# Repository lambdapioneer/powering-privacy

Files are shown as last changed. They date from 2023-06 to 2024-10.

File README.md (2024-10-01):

# Powering Privacy

This repository contains the artifacts from the paper: [Powering Privacy: On the Energy Demand and Feasibility of Anonymity Networks on Smartphones](https://www.usenix.org/conference/usenixsecurity23/).
It is has been submitted to the Artifact Evaluation process and has been awarded all badges we applied for.
You can find the [artifact appendix here](https://www.usenix.org/system/files/usenixsecurity23-appendix-hugenroth.pdf).

USENIX Artifact Evaluation Badge Available
USENIX Artifact Evaluation Badge Functional

## Overview

This repository contains:
- Documentation to build a hardware measurement kit
- Software and instructions to perform macro studies of long-running protocols
- Software and instructions to perform micro studies of individual operations
- Software and instructions to analyze results from these studies and generate plots
- Sample traces to allow evaluation without having to build the hardware kit

To verify these claims for the artifact evaluation process, please follow the [walkthrough.md](walkthrough.md) file.

## Requirements

You need access to a local computer running Ubuntu 20.04 with at least 16GiB of RAM and 200GiB of free disk space.
For the hardware setup, see the [bill of materials](hardware/bill-of-materials.md).

Further, we assume that you are comfortable doing the following tasks:
- Usage of standard developer tools (git, ssh, etc.)
- Basic familiarity with Python 3, Jupyter Notebooks, Android, and Rust
- Creating and running Docker images

We tested the setup with the following software:
- Ubuntu 20.04.6 LTS ([download here](https://releases.ubuntu.com/focal/))
- Python 3.8.10 (installed via apt-get)
- Docker 24.0.4 ([downloaded from here](https://docs.docker.com/engine/install/ubuntu/#install-using-the-convenience-script))
- Rust rustc 1.71.0-stable ([downloaded from here](https://rustup.rs/))
- Android Studio 2022.1.1 ([downloaded from here](https://developer.android.com/studio/archive))
- Gradle wrapper version 7.5 (installed with the tools within the `android` folder)

## Architecture overview

The following diagram shows the architecture of all components.
Note that for many of the steps, you do not need all of them.
The arrows indicate the direction of data flow, not necessarily the order of execution.

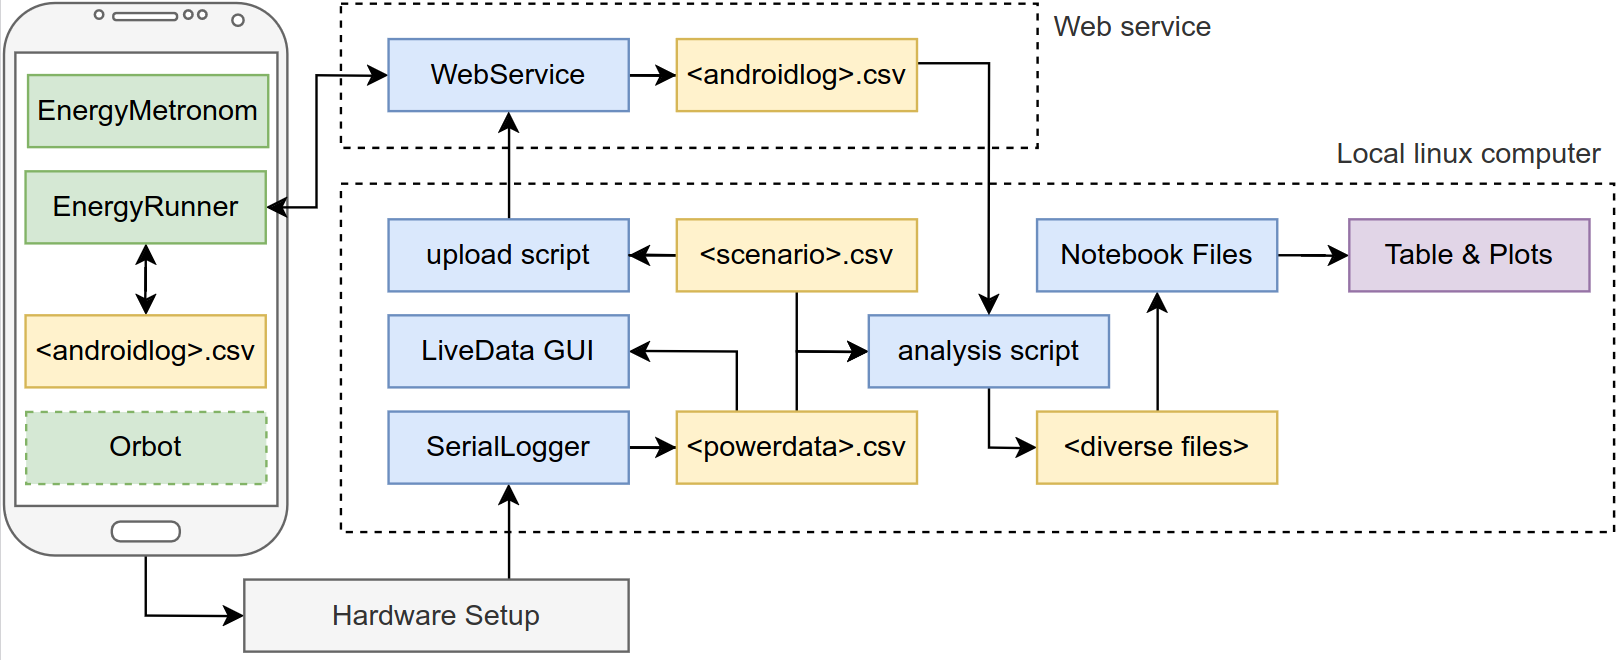
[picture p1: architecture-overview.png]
Architecture overview


The central component of the architecture is the hardware measurement kit.
This is described in [hardware/README.md](hardware/README.md) which contains both assembly and usage instructions.
The measurement kit is placed between the smartphone and the power supply and records the current and voltage over time.

The data is collected on the computer using the [rsoxy serial logger](rsoxy/README.md).
This Rust program reads the custom protocol via a serial connection of USB and stores it in a CSV file in the `/measurements` folder.

At any time the [LiveLogger](livelogger/README.md) can be used to view the so-far recorded power consumption.

## Macro studies

Macro studies measure the power consumption of a protocol over a long period of time.
For this the protocol is started manually on the smartphone, the display is turned off, and then `rsoxy` is started.
The recording is finished by terminating `rsoxy`.

Afterwards the `.csv` data can be analysed using any tool of your choice.
For example, using a Jupyter Notebook as shown in [notebooks/jupyter_tor.ipynb](notebooks/jupyter_tor.ipynb).

## Micro studies

Micro studies measure the power consumption of single operations.
For this, you first create a scenario file such as those in the [scenarios](scenarios) folder.

Then you upload the scenario to the [web service](webservice/README.md) using the [upload-scenarios.sh](scripts/README.md) script.
On the smartphone we use the [EnergyRunner](android/README.md) app to download the scenario.
A USB-to-go adapter and a USB-serial-adapter are used to connect the smartphone to the measurement kit to synchronize their clocks.
This process is described in the [walkthrough.md](walkthrough.md) document.

After the scenario has finished, the serial logger is terminated and on the Android phone the local logs (that contain the timings of individual operations) are uploaded to the web service.
The [analyze.py](scripts/README.md) script can then be used to download the logs, compare them to the local recordings, and break them into the individual sections for the operations.
The resulting `.csv` files can then be analysed using any tool of your choice.
For example, using a Jupyter Notebook as shown in [notebooks/jupyter_crypto_sections.ipynb](notebooks/jupyter_crypto_sections.ipynb).

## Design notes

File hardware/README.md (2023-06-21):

# Hardware

This directory contains all hardware-related files and documentation.

## Overview

The following schematic shows the overall setup. A power sensor (INA219) is placed between smartphone and battery to record the current power consumption. These results are read by an Arduino using the I2C protocol and the logged over USB to a computer. Optionally, a USB-to-go adapter and USB-to-serial component can be used to connect the smartphone to the Arduino to synchronize their clocks for the micro studies.

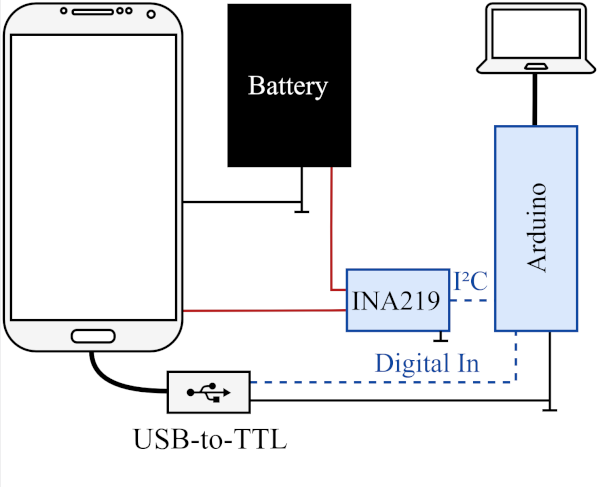
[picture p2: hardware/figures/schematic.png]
Schematic


The following pictures show the full setup in the real world.

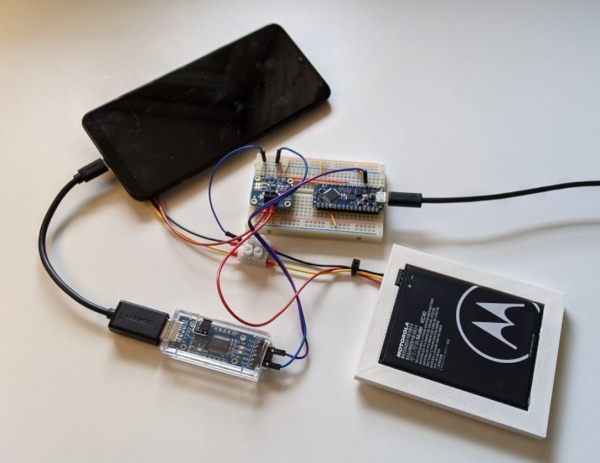
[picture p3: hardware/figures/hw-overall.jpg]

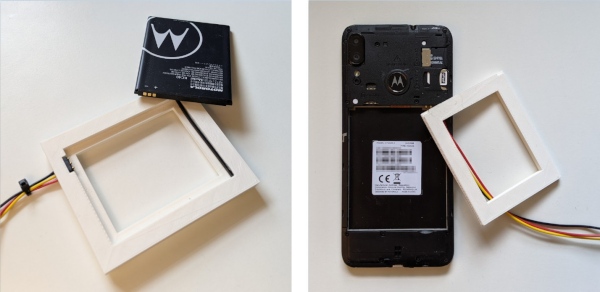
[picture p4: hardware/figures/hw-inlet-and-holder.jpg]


## Setup & Build

For building the hardware kit start by reading both the [Bill of Material](bill-of-materials.md) and the [Assembly Instructions](assembly-instructions.md) completely.

## Usage

Follow the instructions in the [walkthrough](../walkthrough.md) file to learn how to use this kit.

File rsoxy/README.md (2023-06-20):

# RSOXY

This is a fast Rust-based logger for the custom serial port protocol.
It reads from the connected Arduino and appends the data into the given file in a CSV format.
The data can be later read for analysis and during the recording one can `tail -f` that file or follow its updating content using the `livelogger`.

## Setup and build

Install Rust using [rustup](https://rustup.rs/).

For building the `serialport` dependency, the system must have the `libudev` installed.
On Ubuntu, you can do this as follows:

```
$ sudo apt install libudev-dev
```

Then build the project using Cargo:

```
$ cargo build --release
```

## Run

Once built, the binary can be run as follows:

```
$ ./target/release/rsoxy <FILE> [PORT]
```

where `<FILE>` is the path to the file to which the data will be written to and `[PORT]` is the optional path to the serial port device.

The (stderr) output should start with debug information similar to the following:

```
>> # Compiled on 'Apr 13 2021' at '16:13:53'
>> # mps:2897 (limit:2500)
>> # input pin: 14
>> start
```

## Docker

Alternatively, you can build and run the project using Docker. However, this tends to be a bit more quirky than building and running it directly on the host machine.

The following commands build the Docker image and run the container with the serial port device mounted and the measurements volume mounted as well.

```
$ docker build -t rsoxy .
$ docker run -it --volume=$(pwd)/../measurements:/measurements --device=/dev/ttyACM0 --rm rsoxy rsoxy /measurements/myexperiment.csv
```

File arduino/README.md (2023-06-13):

# Arduino

This folder contains the software and instruction to flash the Arduino for the hardware setup.

## Setup and build

Install the Arduino IDE. Then install the Adafruit INA219 library by going to `Tools > Manage Libraries` and searching for `Adafruit INA219`:

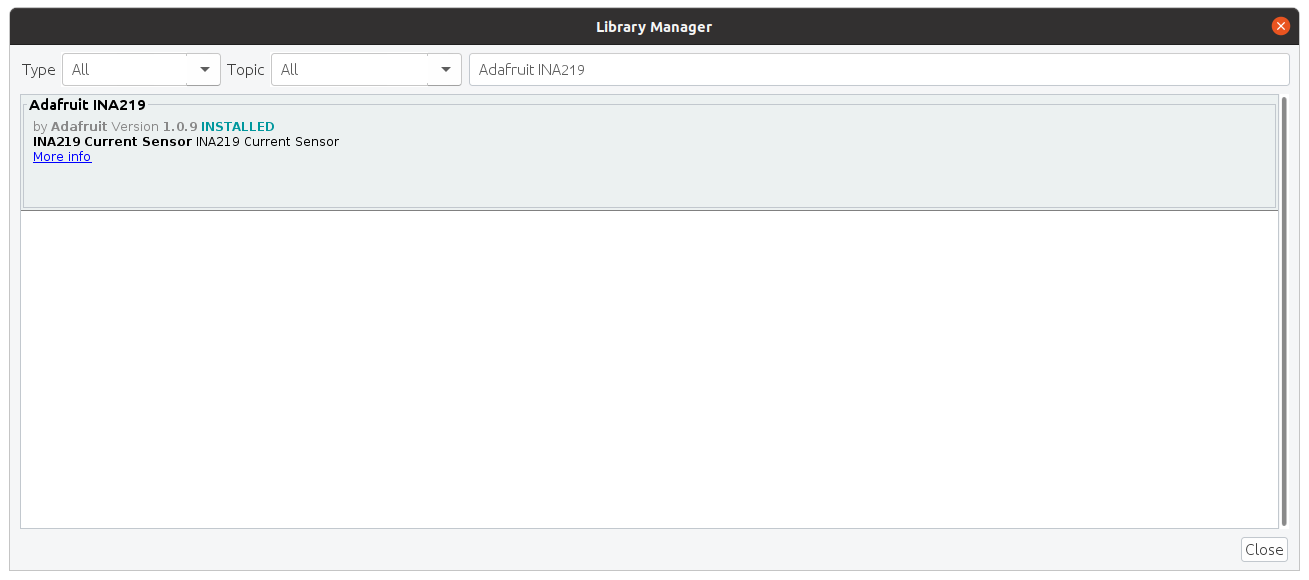
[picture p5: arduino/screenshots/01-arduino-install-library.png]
Installing library


Then open the `logger.ino` file in the Arduino IDE and flash it to the Arduino. Follow the instructions for the other hardware setup in [hardware/README.md](../hardware/README.md).

Alternatively, you can use the `arduino-cli` to build and flash the Arduino:

```bash
$ export FQDN="arduino:megaavr:nona4809"
$ arduino-cli board list
$ arduino-cli compile --fqbn $FQDN logger
$ arduino-cli upload -p /dev/ttyACM0 --fqbn $FQDN logger
```

## Run

When all components have been connected, you can start the Arduino by connecting it to a free USB port on your computer.
Use the [rsoxy](../rsoxy/README.md) serial logger to verify that everything is working correctly.
In particular, watch out for messages that indicate that the INA219 was not found.
The Arduino should reset every time the serial connection is re-started which allows to just restart the serial logger without having to re-connect the Arduino.

## Optional: custom INA219 calibration

By default the `logger.ino` uses a 16V/400mA calibration for the INA219.
However, 400mA might be limiting, and we can increase the range to 800mA as well as increasing the sampling frequency by modifying the library.

To do so, find the libraries folder of the Arduino IDE, open the file `libraries/Adafruit_INA219/Adafruit_INA219.cpp`, and add the following lines below the other `setCalibration_` functions:

```cpp
void Adafruit_INA219::setCalibration_CUSTOM() {
  // 16V & 800mA
  ina219_currentDivider_mA = 20;
  ina219_powerMultiplier_mW = 1.0f;

  ina219_calValue = 8192;
  Adafruit_BusIO_Register calibration_reg =
      Adafruit_BusIO_Register(i2c_dev, INA219_REG_CALIBRATION, 2, MSBFIRST);
  calibration_reg.write(ina219_calValue, 2);

  uint16_t config = INA219_CONFIG_BVOLTAGERANGE_16V |
                    INA219_CONFIG_GAIN_2_80MV |
                    INA219_CONFIG_BADCRES_11BIT |
                    INA219_CONFIG_SADCRES_11BIT_1S_276US |
                    INA219_CONFIG_MODE_SANDBVOLT_CONTINUOUS;

  Adafruit_BusIO_Register config_reg =
      Adafruit_BusIO_Register(i2c_dev, INA219_REG_CONFIG, 2, MSBFIRST);
  config_reg.write(config, 2);
}
```

Also add `void setCalibration_CUSTOM();` to `libraries/Adafruit_INA219/Adafruit_INA219.h`.
Then uncomment the relevant line (l. 53) in `logger.ino`, comment the other old calibration, and flash the Arduino again.

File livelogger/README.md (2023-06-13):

# LiveLogger

The LiveLogger is a GUI interface using Java2D which displays energy measurements.

## Setup and build

Install a JDK 8 or newer. On Ubuntu you do this by running:

```
$ sudo apt-get install openjdk-8-jdk
```

The LiveLogger builds and runs using the Gradle build tooling.
On the first execution, it will first download a recent Gradle version and all dependencies.

Execute the following command to build the live logger:

```
$ ./gradlew build
```

## Run

Execute the following command to run the live logger:

```
$ ./gradlew run
```

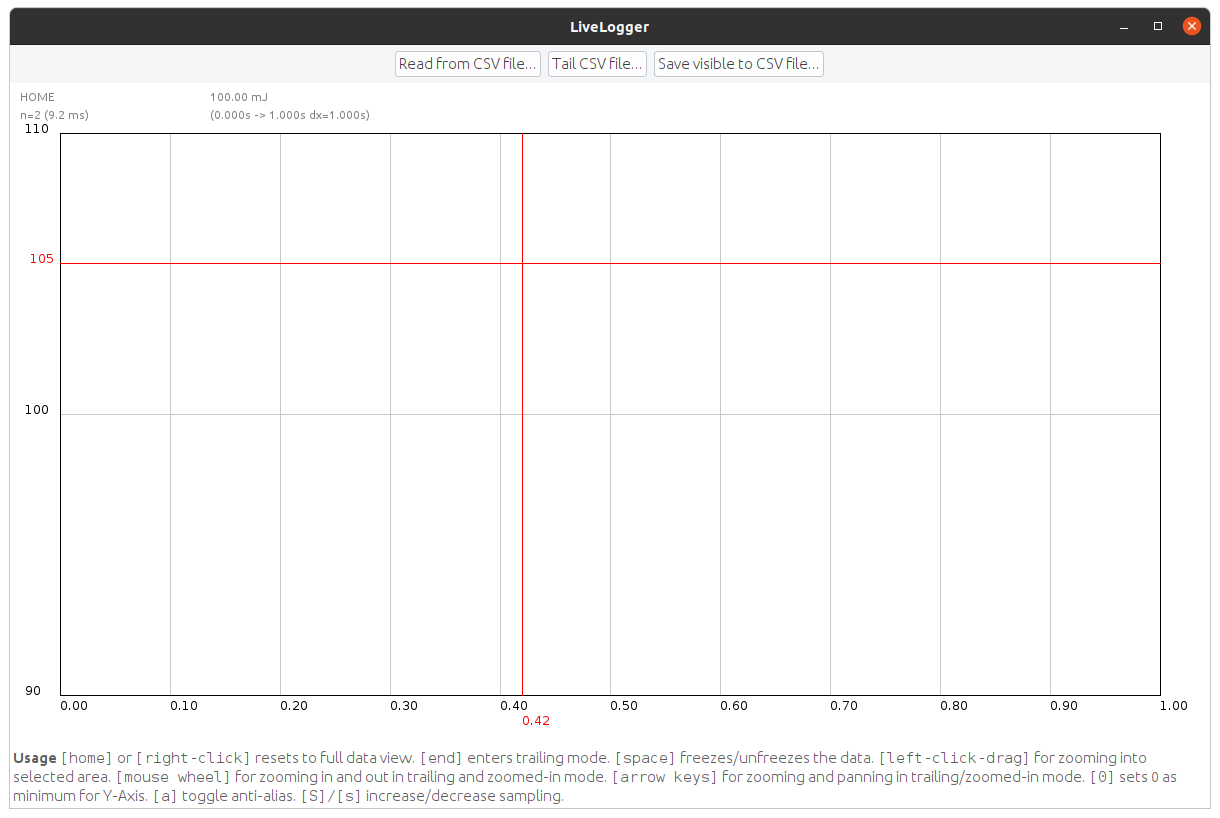
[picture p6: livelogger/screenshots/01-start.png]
Screenshot of the app after start


Once started use the you can use the top buttons to _open_ a recorded file or _tail_ a file that is currently being recorded.
The latter will follow the file like `tail -f`, i.e., continuously read data as it is being appended.

With the data you can use the mouse to select a region of interest.
The plot will then zoom into the selected region.

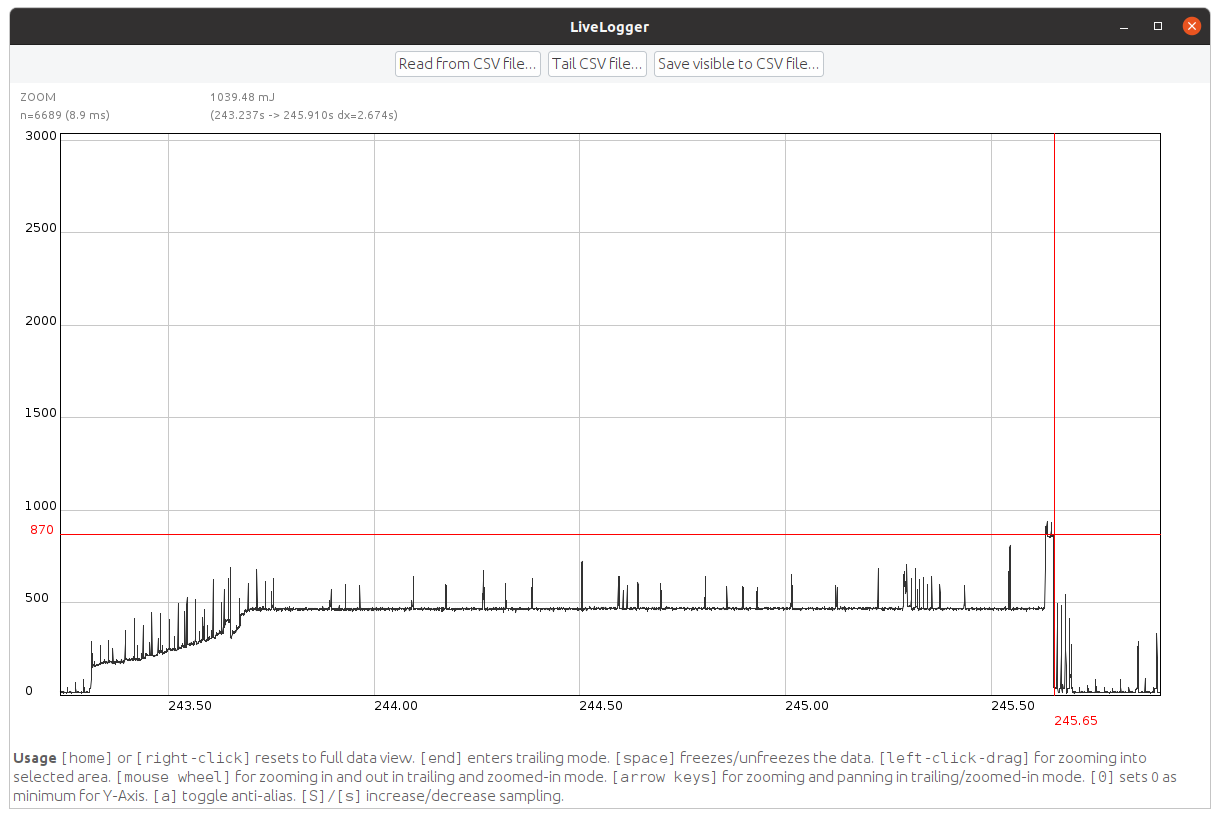
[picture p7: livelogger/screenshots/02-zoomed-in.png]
Screenshot of the app showing a zoomed-in region


Pressing the `HOME` key or a right-click will reset the zoom.
You can also use the left and right arrow keys to move the zoom window.
You can zoom in and out using the mouse wheel and the up and down arrow keys.

When tailing a file you can set the zoom to automatically follow the end of the file by pressing the `END` key.
The current mode is shown in the top-left corner: `HOME`/`ZOOM`/`TAILING`.

The top also shows some basic statistics about the selected region.
Below the mode indicator you can see the number of samples of the current region and how long the draw routine takes.
To the right details about the currently displayed region are shown which include the total energy consumption and the time span.

When displaying many samples, the draw routine can take a long time.
You can improve the performance by turning-off anti-aliasing (key `a`) or increasing the sampling (`shift`+`s`).
However, when saving the currently visible region, the sampling is taken into account, i.e. the saved data will have less resolution.

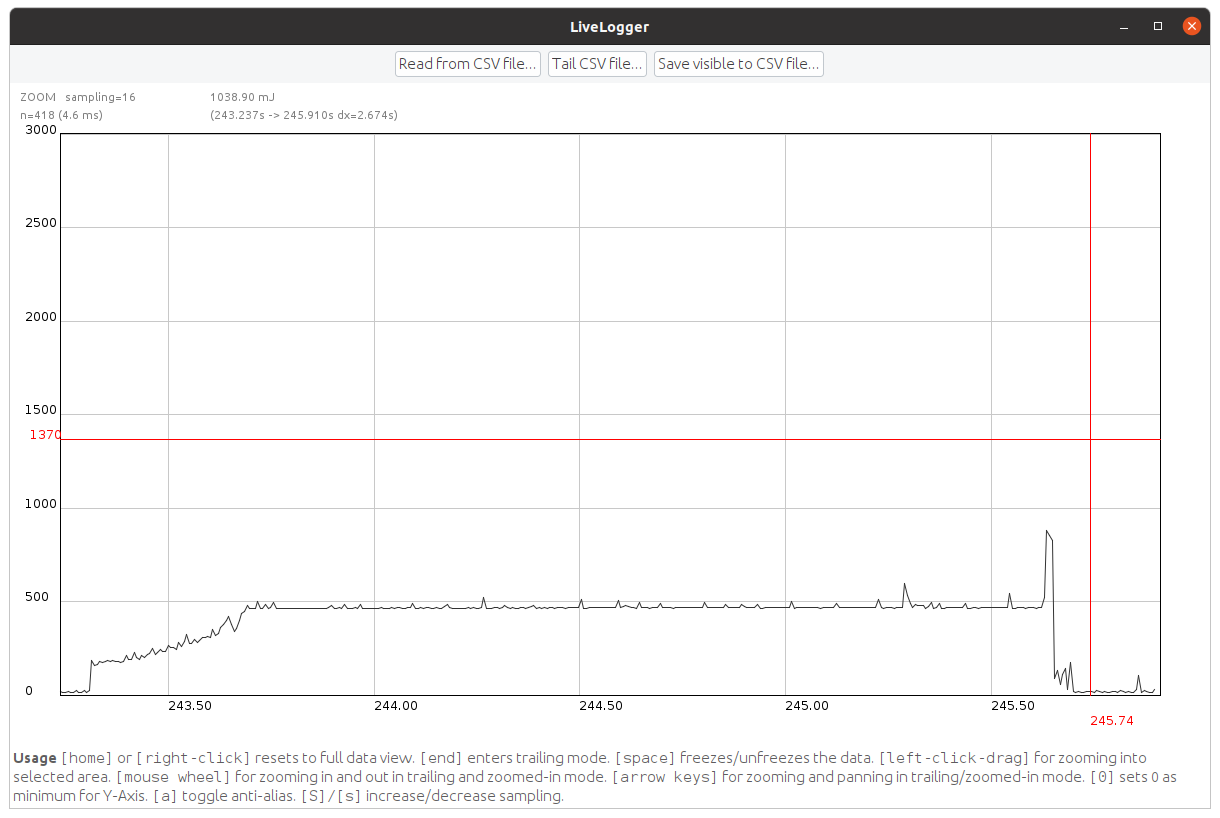
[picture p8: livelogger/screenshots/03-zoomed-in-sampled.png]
Screenshot of the app showing a zoomed-in region while sampled


## Docker

There is no Dockerfile for this component, as the GUI is not really useful in a container.

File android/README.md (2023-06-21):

# Android

This folder contains all Android related project code including libraries and apps.

It consists of two library modules and two app modules.
The `lib_sphinxkt` is a wrapper around the Rust [Sphinx library](https://github.com/nymtech/sphinx).
The `lib_common` library implements many operations used by both apps and depends on the `lib_sphinxkt` library.
The `app_metronom` app allows to execute operations at regular intervals (e.g. opening a web page every 60 seconds).
This is used e.g. for the Tor and VPN macro studies.
The `app_energy_runner` allows to run scenarios files.
These are downloaded from the [web service](../web_service/README.md) and then executed.
This app also synchronizes with the data logger using USB serial and can later upload the timing information for the individual operations.

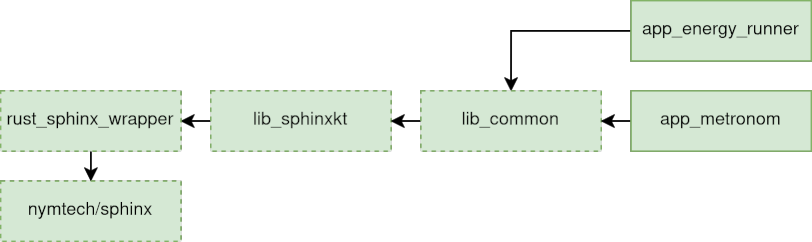
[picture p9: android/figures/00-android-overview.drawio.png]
Overview of components


This folder also contains a `orbot.*.patch` file that can applied to the Orbot source code to add an option for disabling connection padding. See Step E2.2 in the [walkthrough](../walkthrough.md) for details.

## Setup and build

Install Android Studio 2022.2.1 (or newer) and open the project.

The `lib_sphinxkt` uses the Mozilla "Rust Android Gradle Plugin" to build and link the Rust code.
Follow their [setup instruction](https://github.com/mozilla/rust-android-gradle#usage) to setup all dependencies.
You might find that it helpful to first try your local Rust setup with the simpler [rsoxy serial logger project](../rsoxy/README.md).

Before building, update the `configuration.properties` file with the IP address for the web service.

Once you opened the project and installed the Rust Android plugin dependencies, you can build the project (Build > Make Project).

Alternatively, you can build the project from the command line:

```
$ ./gradlew assembleDebug
```

## Run

You can install the `app_metronom` using the following command:

```
./gradlew app_metronom:installDebug
```

After install find the app in the launcher drawer and drag it to the start screen.
Go to the Android app info (usually long press on the icon), navigate to "Advanced" and enable "Display over other apps".
This is required to show the overlay window for the web browsing task.
One starting the app you should see a screen like the following below.
Select a short pause, click `Start`, and observe after 60 seconds that an overlay window appears that loads a website and closes on finish.

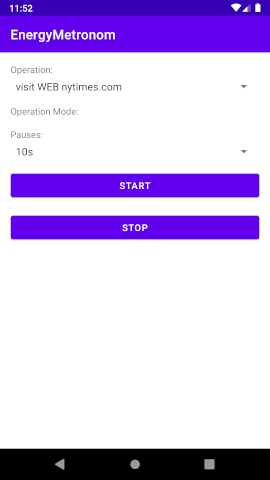
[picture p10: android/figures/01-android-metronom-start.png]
app_metronom after start
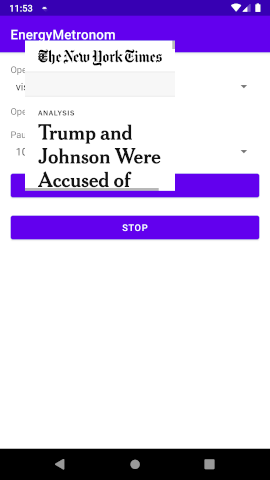
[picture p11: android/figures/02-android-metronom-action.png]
app_metronom during_web_page_load
 

You can install the `app_energy_runner` using the following command:

```
./gradlew app_energy_runner:installDebug
```

After install find the app in the launcher drawer and drag it to the start screen.
Go to the Android app info (usually long press on the icon) and deactivate any battery optimization that might interfere with running the app in the background for long periods of time.
One starting the app you should see a screen like the following below.
The details on how to use the app are given in the complete AE run-through instructions.

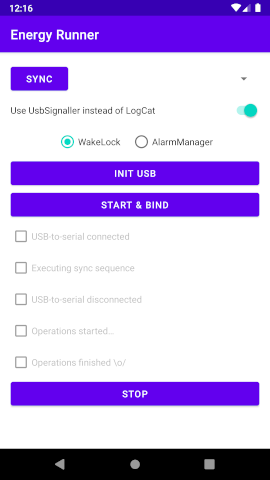
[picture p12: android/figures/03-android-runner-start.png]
app_runner after start


## Docker

There is no Dockerfile for this component, as there is no reliable image for Android development that includes Rust components.

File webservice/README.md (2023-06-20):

# Webservice

The webservice can be run locally or remotely and provides a REST API to sync scenarios to the Android device and to sync the results back.

> **Warning**
> Note that this is a very simple implementation and does not provide any security or authentication.
Hence, if the service is run from a publicly accessible server, it should be protected by a reverse-proxy with authentication or similar.
See the sample .htpasswd file for the sample user/password configuration (user:uyaeNiyaighiu4HaingohShee2ie9ahs).

## Setup and build

Ensure that a version of Python 3 is installed.

First setup the virtual environment and install all required dependencies:

```
$ python3 -m venv venv
$ source venv/bin/activate
(env)$ pip install -r requirements.txt
```

## Run

Start the webservice with the virtual environment activated as follows:

```
(env)$ FLASK_APP=app.py flask run
```

You can verify that the service is running correctly by opening http://127.0.0.1:5000/energy/android_logs.zip which should download an empty .zip archive.

Update the scripts and the Android apps with the correct IP address of the webservice and authentication details (if applicable).

## Docker

Alternatively, you can build and run the project using Docker:

```
$ docker build --network=host -t webservice .
$ docker run -it --rm --volume=storage:/usr/src/webservice/measurements --publish=5000:5000 webservice
```

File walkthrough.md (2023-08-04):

# Artifact Evaluation Walkthrough

This document walks you step-by-step through all three artifact evaluation experiments:

- **E0:** Building and testing all critical components including the hardware kit, rsoxy, and the live logger.
- **E1:** Performing a micro study to measure individual cryptographic operations
- **E2:** Performing a macro study to measure the performance of Tor vs direct website access over WiFi

The experiments provide time estimates in _human-hours_ which are the total work time, which can be interrupted, and _experiment-hours_ which are the durations of the experiments which cannot be interrupted.

## Requirements & preparations

You will need a local computer with:
- A recent Ubuntu version (we tested 20.04)
- At least 16 GiB RAM
- At least 200 GiB free disk space
- A free USB port to connect to the Arduino
- A WiFi where you can connect the smartphone and the computer to the same network

In preparation for building the individual components, you should install the following dependencies before beginning:  

- Docker; see the [Docker documentation](https://docs.docker.com/engine/install/ubuntu/)
- Rust; see the [rustup website](https://rustup.rs/)
- Python 3; it is usually preinstalled; otherwise see the Ubuntu documentation
- Android Studio; see the [Android Studio website](https://developer.android.com/studio/install)

If you use the sample traces, see [measurements/sample-traces/README.md](measurements/sample-traces/README.md) for instructions on how to extract and import them.

## E0: Building and testing all critical components (2-20 human-hours + 1×1 experiment-hour)

In this experiment you will first (optionally) build the hardware kit and then use it with the `rsoxy` and `livelogger` programs to record a test trace. This will ensure that all components are working correctly and that you are familiar with the process of recording a trace.

### E0.1: Building the hardware kit (optional: 9 human-hours, 12 hours wait time)

> **Note**
> You can skip this step if you have been provided the hardware kit or are using the sample traces.

First read the [bill of materials](hardware/bill-of-materials.md) to see what you need to build the hardware kit. Then follow the [assembly instructions](hardware/assembly-instructions.md) to build the hardware kit.

Then follow the [Arduino setup instructions](arduino/README.md) to program the Arduino.

### E0.2: Test rsoxy and live logger (1 experiment-hour)

Follow the instructions in the [rsoxy/README.md](rsoxy/README.md) to build rsoxy. 
Follow the instructions in the [livelogger/README.md](livelogger/README.md) to build livelogger. 

Connect the Arduino still to the computer, ensure that the final assembly of the hardware kit with the battery in the battery holder and the inlet inside the smartphone, and turn on the smartphone.
Start recording a test trace with `rsoxy` in `measurements/e0-test-trace.csv`.

> **Note**
> If you use the sample traces, copy the `e0/demo_trace_wifi_display_onoff_20230620_1600.csv` file to your `/measurements` directory.

The first lines of (stderr) output from `rsoxy` should look like this:

```
>> # Compiled on 'June 1 2023' at '13:37:42'
>> # mps:2897 (limit:2500)
>> # input pin: 14
>> start
```

Open the `livelogger` and tail the current measurement file. You should see the data being logged in real-time and change as you use the device. For instance, try changing the display brightness or turn the display off and observe how it enters low-power mode after a few seconds. If you are using the sample file, you should see high power consumption at the beginning (with a small dip where the brightness of the display is changed), and then lower power after the display is turned off.

The GUI should look similar to this:

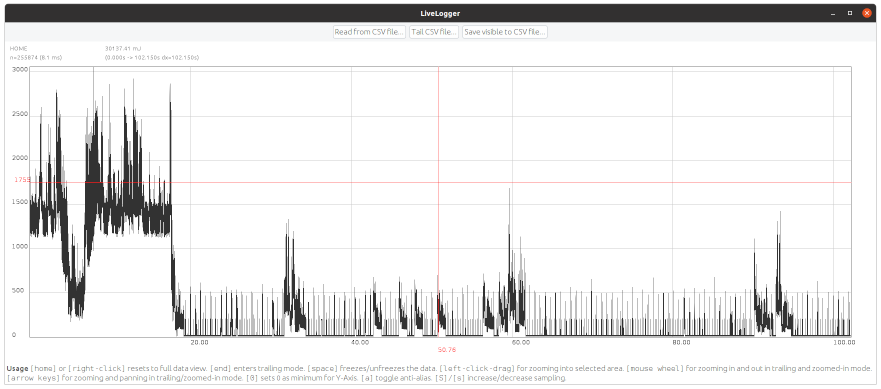
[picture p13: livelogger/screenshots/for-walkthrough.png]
livelogger GUI


If you got to here, well done! Most of the dependencies and configurations are now set up and you can proceed to the next steps. If built your own hardware kit, you can be quite confident that it is working correctly.

## E1: Micro study of cryptographic operations

In this experiment you use the most complex experiment setup to first load a scenario to the Android phone, then record it with synchronized clocks, download and combine all logs, and then re-create Table 2 from the paper.

> **Note**
> If you use the sample traces, copy the files from `e1/` file to your `/measurements` directory and skip to step E1.6.

### E1.1: Create the scenarios

The scenarios have been created for you, and you can inspect the files [scenarios/crypto_asymmetric.scenario](scenarios/crypto_asymmetric.scenario) and [scenarios/crypto_hashing.scenario](scenarios/crypto_hashing.scenario).

### E1.2: Start the webservice and upload the scenarios (1 human-hours)

Next we will build and run the webservice on the local computer. Alternatively, if could be run on a remote server, but this is more complicated and not necessary for the artifact evaluation. Follow the instructions in [webservice/README.md](webservice/README.md) to build and run the webservice. Either the local Python 3 approach or using Docker is fine.

However, verify that it is reachable from the Android phone when connected to the same WiFi. Try opening `http://<computer-wifi-ip-here>:5000/energy/android_logs.zip` in the browser on the Android phone and verify that it downloads an empty zip file.

Keep the webservice running for the rest of the experiment.

Follow the instructions in [scripts/README.md](scripts/README.md) to run the `upload_scenarios.sh` script.

### E1.3: Build and install the Android app (2 human-hour)

Follow the instructions in [android/README.md](android/README.md) to build and install the `energy_runner` Android app. For this you might need to [enable the developer mode](https://developer.android.com/studio/debug/dev-options) on the smartphone.

This is also a good time to remove or disable all unwanted apps so that they do not interfere with the experiment. Also, long press on the app, go to the app info, and disable _all_ battery optimizations. This is important to ensure that the app is not killed in the background.

Once the app is started, press the `SYNC` button to download the scenarios. They should appear in the top list. If you see an error, check the logs in the Android Studio logcat console.

Connect the USB-to-serial adapter to the USB-OTG cable and plug it into the smartphone. You should see a popup that asks you to start EnergyRunner. Confirm and select the box to always use it. Remove the adapter and force-stop the app.

### E1.4: Run the experiments (2×1 experiment-hour)

Connect the USB-to-serial adapter to the breadboard as per Step 6 in the [assembly instructions](hardware/assembly-instructions.md). Connect the USB-OTG with the adapter and the smartphone. This should now start the EnergyRunner app automatically.

Once inside the app press `SYNC` and then enter flight mode to to avoid any background network traffic. Select the scenario that you want to run first. Press `INIT USB` after which the one indicator LED on the Arduino should turn off.

On your local computer start `rsoxy` to record a file into `measurements/<scenario-name>_<yyyymmdd>_<hhmm>_raw.csv` (e.g. `measurements/crypto_asymmetric_20230620_1600_raw.csv`). The exact naming and semi-accurate datetime is important as the analysis script will use the filenames to determine which recordings belong together.

Optionally, start `livelogger` to tail the file and observe the recording as it progresses.

On the smartphone press `START` and turn off the display.

The smartphone should say "USB is connected" once it starts using the serial adapter. On the computer you should be able to observe the synchronization pattern as 1s and 0s in the stderr output of `rsoxy`.

Once the smartphone says "Sync is done", disconnect the USB-OTG cable. The smartphone should soon after confirm this by saying "USB is disconnected". The text-to-speech output is used to avoid having to turn on the screen.

Now wait patiently while the experiment is under way. Both experiments should take around 30 minutes to complete. Once the scenario is completed, the smartphone will repeatedly say "Operations finished".

Once finished, stop `rsoxy` (CTRL+C) and on the Android phone press `STOP`. Turn on WiFi and press `SYNC` to upload the Android logs to the webservice. If the upload fails, it is possible to retry multiple times as the log files are stored locally as well.

Repeat the experiment for the other scenario.

### E1.5: Download and analyze the logs (1 human-hour)

On the computer run the `analyze.py` script (see [scripts/README.md](scripts/README.md)) to download and analyze the logs. It takes the scenario filename as its mandatory command line argument.

Once finished, for every scenario name, there should be the following files in the `measurements` directory:

- `_raw.csv`: the power measurements created with `rsoxy`
- `_android.csv`: the Android logs created by the EnergyRunner app
- `_trace.csv`: additional Android logs created by the EnergyRunner app
- `_info.json`: JSON file with the clock difference information
- `_sections.csv`: the timing information and calculated energy consumption for each operations.

For the final step, the Jupyter Notebooks will only use the `_sections.csv` file, but the other files are useful for debugging and verification.

### E1.6: Run Jupyter Notebooks (1 human-hour)

Follow the instructions in [notebooks/README.md](notebooks/README.md) to run the `notebooks/jupyter_crypto_sections.ipynb` notebook. If you use your own measurements, update the filenames in the second cell.

The output of the table should look like this:

```latex
\midrule
Gen RSA-1024 & 116.47 & 76.36 \\ 
Gen RSA-2048 & 796.05 & 597.84 \\ 
Gen RSA-4096 & 2898.43 & 2042.77 \\ 
Sign RSA-1024 & 1.88 & 0.35 \\ 
Sign RSA-2048 & 6.22 & 1.22 \\ 
Sign RSA-4096 & 26.73 & 4.68 \\ 
Verify RSA-1024 & 0.34 & 0.10 \\ 
Verify RSA-2048 & 0.50 & 0.08 \\ 
Verify RSA-4096 & 0.75 & 0.10 \\ 
\midrule
Gen EC-224 & 1.11 & 0.06 \\ 
Gen EC-256 & 0.51 & 0.05 \\ 
Gen EC-384 & 2.65 & 0.07 \\ 
Gen EC-521 & 5.25 & 0.27 \\ 
Sign EC-224 & 1.43 & 0.15 \\ 
Sign EC-256 & 0.83 & 0.18 \\ 
Sign EC-384 & 3.24 & 0.16 \\ 
Sign EC-521 & 6.27 & 0.10 \\ 
Verify EC-224 & 1.52 & 0.05 \\ 
Verify EC-256 & 1.54 & 0.08 \\ 
Verify EC-384 & 3.43 & 0.07 \\ 
Verify EC-521 & 6.74 & 0.15 \\ 
\midrule
Sphinx (1x) & 9.66 & 0.31 \\ 
Sphinx (10x) & 86.34 & 8.07 \\ 
Sphinx (100x) & 842.44 & 11.40 \\ 
```

## E2: Macro study of Tor

In this experiment you measure long protocol runs and save them in individual files. In particular, you will measure the energy consumption of Orbot over WiFi for both the idle and web browsing scenarios and then compare it with not using Tor.

> **Note**
> If you use the sample traces, copy the files from `e2/` file to your `/measurements` directory and skip to step E2.4.

### E2.1: Install EnergyMetronom (1 human-hour)

Follow the instructions in [android/README.md](android/README.md) to build and install the `metronom` Android app. Afterwards, long press on the app and go to the app info. There, enable "Display over other apps" which is required to show the overlay window for the web browsing task. Also, and disable _all_ battery optimizations. This is important to ensure that the app is not killed in the background.

Test the app by selecting the settings to open the news website every 10 seconds and observe that an overlay window appears and disappears.

### E2.2: Install Orbot (1 human-hour)

Clone the [Orbot repository](https://github.com/guardianproject/orbot/) and checkout commit `b06e05c4` (version 16.6.0-RC4). Install the app following their instructions and using `./gradlew installFullpermRelease`. As this is a release build, you might need to create a signing key first (see https://developer.android.com/studio/publish/app-signing#generate-key).

Test the app on the device. In particular, enable VPN mode and verify that you can access regular websites through Tor. This can be done by opening https://check.torproject.org/ in the phone browser.

In the setting make sure to _enable_ "Connection padding" and _disable_ "Reduced connection padding". This ensures that regular connection padding is forced on. 

> **Note**
> For our experiments we have written a [patch file](android/orbot-add-setting-to-disable-connection-padding.patch) that adds a new setting to disable connection padding. This is not needed for the walkthrough, but you might want to apply it if you run your own experiments.

### E2.3: Run the experiments (4×1 experiment-hour)

Now you will run four experiments to measure the power consumption of all combinations. In the terminology of the later Jupyter notebook scripts we will have:

- `radio`:
  - `wifi`
- `activity`:
  - `idle`
  - `web`
- `networks`
  - `direct` (i.e. no Tor)
  - `fullpad` (i.e. Tor with full padding)

As you record the power consumption with `rsoxy`, make sure to name them according to this scheme: `measurements/tor_<radio>_<activity>_<network>.csv` (e.g. `measurements/tor_wifi_idle_direct.csv`). This is important as the analysis script will use the filenames to find the recordings.

As you record you can use the livelogger tool to observe the current measurements to quickly identify andy issues.

Now run the following experiments:

- `activity=idle`
  - `network=direct`
    - Turn off the display, wait 30 seconds and then record the energy measurements for at least 10 minutes.
  - `network=fullpad`
    - Enable Tor in VPN mode with the settings from above. Turn off the display, wait 30 seconds and then record the energy measurements for at least 10 minutes.
- `activity=web`
  - `network=direct`
    - Start the metronom with visiting the website every 60 seconds. Wait until it was displayed successfully one time. Then turn off the display, wait 30 seconds and then record the energy measurements for at least 10 minutes.
  - `network=fullpad`
    - Enable Tor in VPN mode with the settings from above. Start the metronom with visiting the website every 60 seconds. Wait until it was displayed successfully one time. Then turn off the display, wait 30 seconds and then record the energy measurements for at least 10 minutes.

Afterwards, you should have the following files (each around 20-25 MiB in size) in your measurements directory:

```
tor_wifi_idle_direct.csv
tor_wifi_idle_fullpad.csv
tor_wifi_web_direct.csv
tor_wifi_web_fullpad.csv
```
  
### E2.4: Analyse the measurements (1 human-hour)

Follow the instructions in [notebooks/README.md](notebooks/README.md) to run the `notebooks/jupyter_tor.ipynb` notebook.

The graph output should look like this:

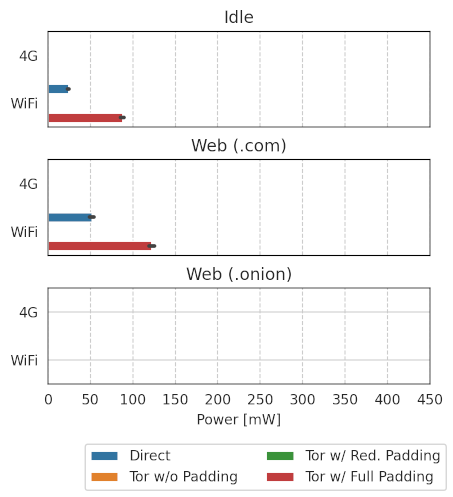
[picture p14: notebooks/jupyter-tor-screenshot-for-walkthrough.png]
Plot output


And the table output should look like this:

```latex
\multicolumn{4}{c}{\textit{Idle}}\\
\midrule
4G & Direct & nan & nan\% \\ 
4G & Tor w/o Padding & nan & nan\% \\ 
4G & Tor w/ Red. Padding & nan & nan\% \\ 
4G & Tor w/ Full Padding & nan & nan\% \\ 
\midrule
WiFi & Direct & 23.4 & 0.3\% \\ 
WiFi & Tor w/o Padding & nan & nan\% \\ 
WiFi & Tor w/ Red. Padding & nan & nan\% \\ 
WiFi & Tor w/ Full Padding & 87.3 & 1.1\% \\ 
\midrule
\multicolumn{4}{c}{\textit{Web (.com)}}\\
\midrule
4G & Direct & nan & nan\% \\ 
4G & Tor w/o Padding & nan & nan\% \\ 
4G & Tor w/ Red. Padding & nan & nan\% \\ 
4G & Tor w/ Full Padding & nan & nan\% \\ 
\midrule
WiFi & Direct & 52.0 & 0.6\% \\ 
WiFi & Tor w/o Padding & nan & nan\% \\ 
WiFi & Tor w/ Red. Padding & nan & nan\% \\ 
WiFi & Tor w/ Full Padding & 122.9 & 1.5\% \\ 
\midrule
\multicolumn{4}{c}{\textit{Web (.onion)}}\\
\midrule
4G & Direct & nan & nan\% \\ 
4G & Tor w/o Padding & nan & nan\% \\ 
4G & Tor w/ Red. Padding & nan & nan\% \\ 
4G & Tor w/ Full Padding & nan & nan\% \\ 
\midrule
WiFi & Direct & nan & nan\% \\ 
WiFi & Tor w/o Padding & nan & nan\% \\ 
WiFi & Tor w/ Red. Padding & nan & nan\% \\ 
WiFi & Tor w/ Full Padding & nan & nan\% \\ 
\midrule
```

Note that some bars and entries are missing when comparing to the table. These are because we only recorded a subset of the parameter space.

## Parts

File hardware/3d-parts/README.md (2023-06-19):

# 3D Printed Parts

Both hardware parts are designed using [OpenSCAD](https://openscad.org/) and maintained within the respective `.scad` files.
From these the STL files are rendered.
You should use the slicing tool that is recommended for your 3D printer to generate the respective `.gcode` files.
For reference, the folder contains some for the Pruse i3 MK3S.

## Renderings

This is the **battery replacement** which goes into the phone. Note the corners that allow it to snap into place. Also, there are three cut-outs for the contacts.

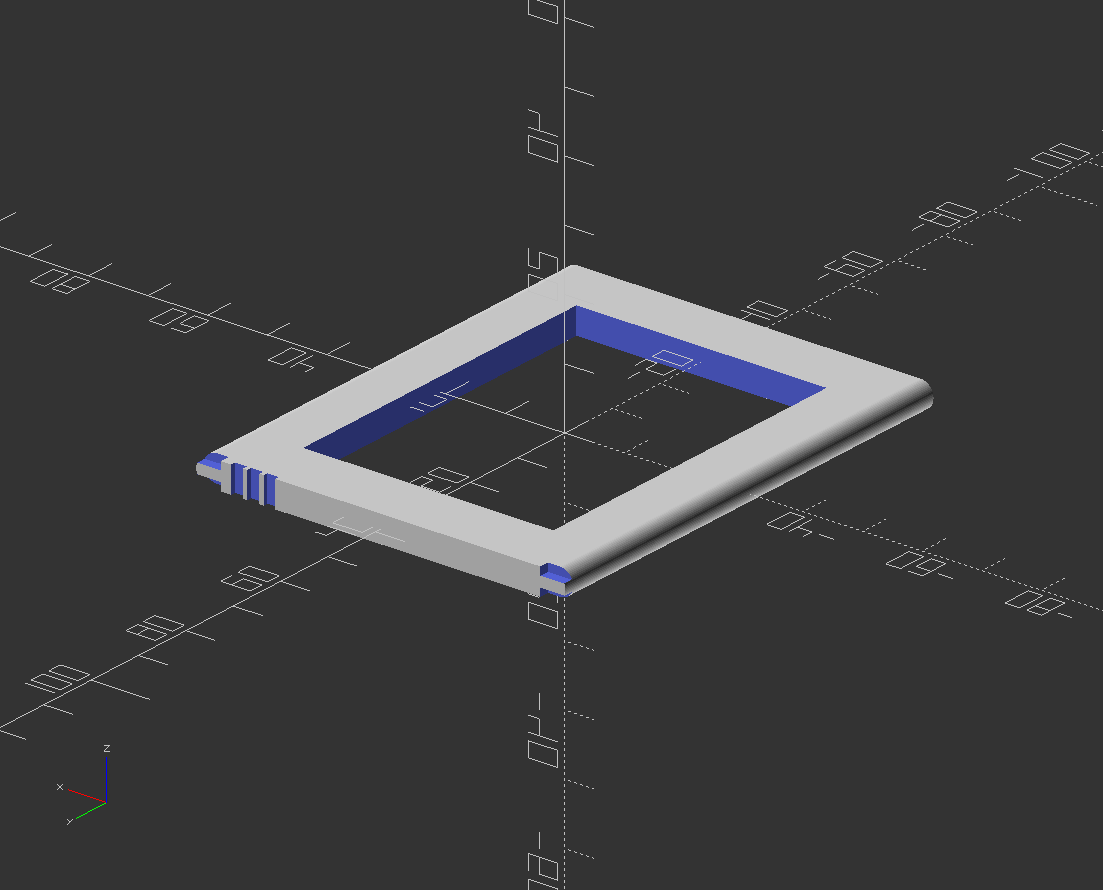
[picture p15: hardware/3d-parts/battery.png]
The battery replacement


This is the **battery holder** which holds and connects the actual battery. Note the hole (front left) where the battery connector slides in.

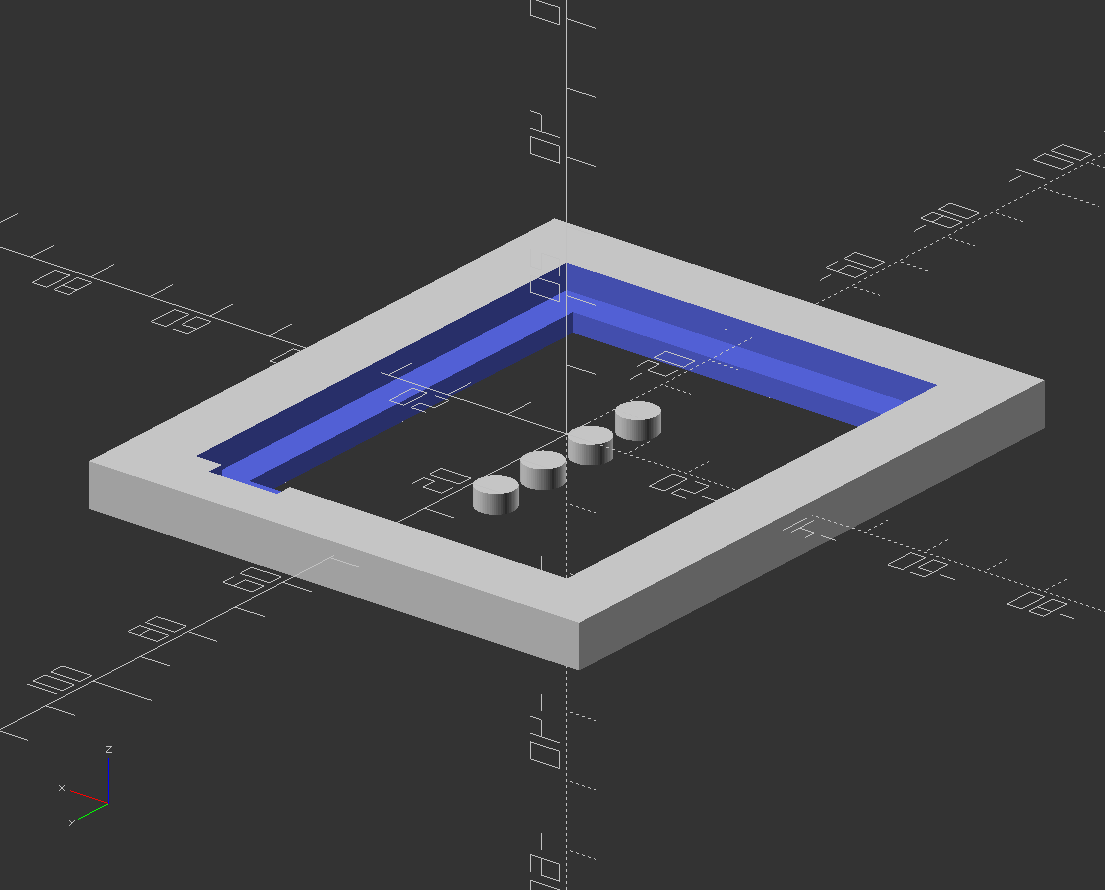
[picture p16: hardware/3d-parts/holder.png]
The battery holder


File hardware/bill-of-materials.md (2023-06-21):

# Bill of materials

This document lists all parts that are required for the project. It is split into three sections: parts, tools and consumables.
We believe that the required tools and consumables are commonly available in most makerspaces.

## Parts

The links are just to help disambiguate the parts. They are available from various sources.

| Part | Quantity | Comment & Link |
| ---- | -------- | -------------- |
| Arduino Nano Every | 1 | [Link to arduino.cc](https://docs.arduino.cc/hardware/nano-every) |
| INA219 | 1 | On a breakout board; [link to adafruit.com](https://www.adafruit.com/product/904) |
| Breadboard | 1 | Half-size; [link to adafruit.com](https://www.adafruit.com/product/4539) |
| Leaf battery connector | 1 | TE 1981061-1; [link to te.com](https://www.te.com/usa-en/product-1981061-1.html) |
| USB-to-serial adapter | 1 | With FTDI FT232RL chip; [link to amazon.com](https://www.amazon.com/gp/product/B07BBPX8B8/)
| USB OTG cable | 1 | For example: [link to amazon.com](https://www.amazon.com/UGREEN-Adapter-Samsung-Controller-Smartphone/dp/B00LN3LQKQ/) |
| Motorola Moto E6 Plus | 1 | Available from third-party vendors; [link to gsmarena.com](https://www.gsmarena.com/motorola_moto_e6_plus-9831.php) |

## Tools

| Tool | Comment |
| ---- | -------------- |
| Soldering station |  |
| 3D printer | We use a Prusa i3 |
| Wire cutter | |
| Crimping tool | (for Ferrules) |
| Wire stripper | (optional) |
| Tweezers ||
| Screwdrivers | Various small ones|

## Consumables

| Part | Quantity | Comment & Link |
| ---- | -------- | -------------- |
| Breadboard wires | various ||
| Wires | 2m | For connecting battery and smartphone, at least 16 AWG |
| Ferrules | 10 | For the above mentioned wires |
| 6.8kΩ resistor | 1 | |
| Male to female jumper wires | 2 | |
| Terminal connector blocks | 3 | Small ones (~5A) |
| SD card (adapter) | 1 | We use the connectors for the battery inlet |
| Solder wire |||
| 3D printing material |||
| Two-part epoxy | 1 | For example "Araldite Rapid" |
| Gloves | | For handling epoxy |

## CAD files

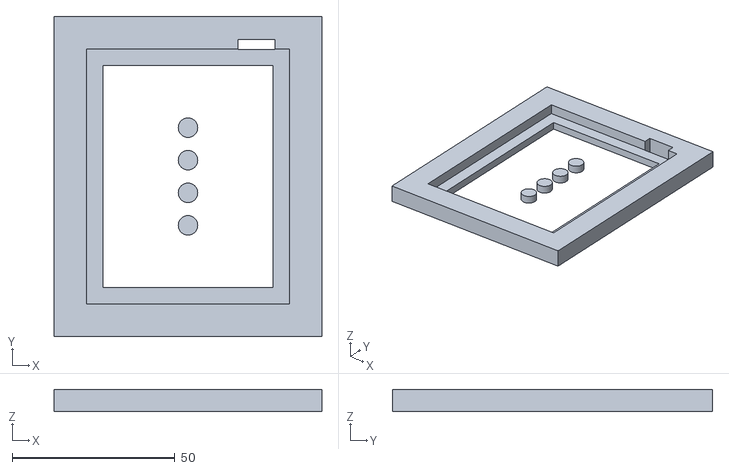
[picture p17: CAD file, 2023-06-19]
hardware/3d-parts/holder.stl
82.3 x 98.3 x 6.90

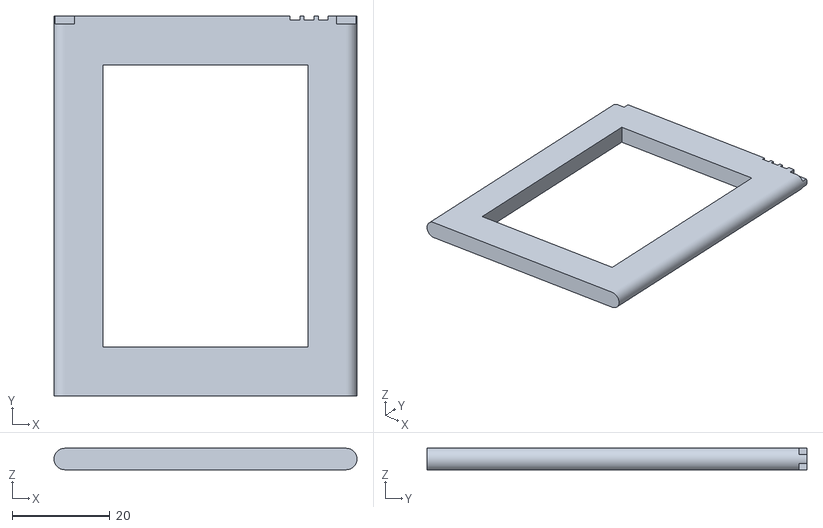
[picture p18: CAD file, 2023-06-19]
hardware/3d-parts/battery.stl
62.0 x 77.7 x 4.40

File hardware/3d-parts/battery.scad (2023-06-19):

$fn=64; 

// total measurements
tw = 62.0;
td = 77.7;
th = 4.4;

// cylinders
r = th / 2;

// block
bw = tw - r - r;

// edges for the battery holding slots
ew = 2.0;
eh = (4.4-1.7)/2;
ed = 1.4+0.2;

// optional inner hole padding
ip = 20;

difference () {
    union () {
        cube([bw, td, th], true);
        translate ([bw/2,td/2,0]) {
            rotate ([90,0,0]) {
                cylinder(td, r, r);
            }
        }
        translate ([-bw/2,td/2,0]) {
            rotate ([90,0,0]) {
                cylinder(td, r, r);
            }
        }
    }
    
    // edges to slot in
    translate ([bw/2,td/2,th/2]) {
        cube([ew*2, ed*2, eh*2], center=true);
    }
    translate ([bw/2,td/2,-th/2]) {
        cube([ew*2, ed*2, eh*2], center=true);
    }
    translate ([-bw/2,td/2,th/2]) {
        cube([ew*2, ed*2, eh*2], center=true);
    }
    translate ([-bw/2,td/2,-th/2]) {
        cube([ew*2, ed*2, eh*2], center=true);
    }
    
    // empty middle (to save material and time)
    cube([tw-ip, td-ip, th+1], center=true);
    
    // small spaces for the contacts
    sw=2.0;
    sfromside=6.9;
    sinterval=2.9;
    sd=0.8;
    for ( x = [0 : sinterval : 2*sinterval] ){
        sc=tw/2-sfromside;
        translate ([sc-x,td/2,0]) {
            cube([sw, 2*sd, th+0.1], center=true);
        }
    }
}

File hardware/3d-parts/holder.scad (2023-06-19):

$fn=64; 

// total measurements (inner bay)
tw = 62.3;
td = 78.3;
th = 3.9;//4.4;
t_pins_from_right = 10.1; // center pin

// outer padding
op = 20.0;

// inner padding
ip = 10;

// support height
sh = 3.0;

// TE battery holder 1981061-1
bh_w = 11.2+0.3; // extra for tolerance
bh_d = 2.9+0.2;
bh_h = 7.6;
bh_pins_h = 5.8;

// position relative to center pin
module battery_holder () {
    translate ([0, bh_d/2, bh_pins_h - bh_h]) {
        color ([1.0, 0, 0]) {
            cube([bh_w, bh_d, bh_h], center=true);
        }
    }
}

// main part
difference () {
    union () {
        cube([tw+op, td+op, th], center=true);
        translate ([0, 0, -(th/2+sh/2)]) {
            cube([tw+op, td+op, sh], center=true);
        }
    }
    cube([tw, td, th+0.1], center=true);
    cube([tw-ip, td-ip, th+10],center=true);
    
    translate ([tw/2-t_pins_from_right,td/2-0.1,0]) {
        battery_holder();
    }
}

// legs

lr = 3;
lh = 3;
translate ([0, 0, -(th/2 + sh)]) {
    translate([0, -15, 0]) { cylinder(lh, lr, lr); }
    translate([0, -5, 0]) { cylinder(lh, lr, lr); }
    translate([0, 5, 0]) { cylinder(lh, lr, lr); }
    translate([0, 15, 0]) { cylinder(lh, lr, lr); }
}

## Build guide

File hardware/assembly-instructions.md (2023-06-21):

# Assembly instructions

Read the entire documentation before starting to build the hardware kit.

> **Warning**
> Working with batteries of any kind is dangerous. Only continue if you are certain that you know how to use the setup safely. In particular: if there are any deformations, heat, or smoke, disconnect everything immediately and bring the battery outside using a fire-safe container.

## Step 1: breadboard assembly (1 hour)

**Required tools:** Soldering station, wire cutter, wire stripper

**Required skills:** Soldering, working with breadboards

**Required material:** Arduino Nano Every, INA219, Breadboard, 6.8kΩ resistor, Breadboard wires

First, follow the instructions for the Arduino and INA219 components to finish their break out assembly. Typically, this involves soldering the header pins to the components. 

Then, connect the components on the breadboard as shown in the following image:

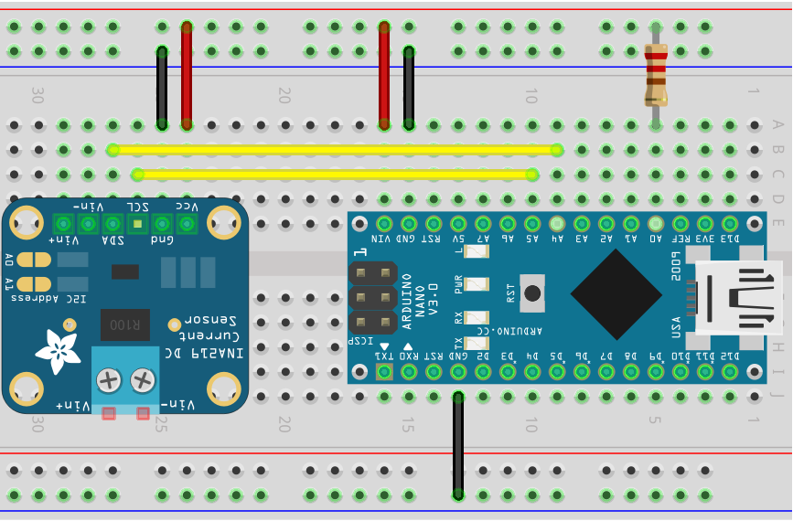
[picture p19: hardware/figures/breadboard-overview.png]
Breadboard assembly


Note that the resistor is 6.8kΩ, and not as shown in the picture 220Ω. Your Arduino and INA219 breakout boards might look differently.

You can now test this setup using the instructions in the [Arduino section](../arduino/README.md). Together with the [rsoxy](../rsoxy/README.md) serial logger, you should be able to see measurements of ~0mW.

## Step 2: 3D print components (4 hours)

**Required tools:** 3D printer, slicer software

**Required skills:** 3D printing

**Required material:** 3D printing material

Use the files and instruction in the [3D parts](../3d-parts/README.md) section to print the required components. You should end up with the following parts:

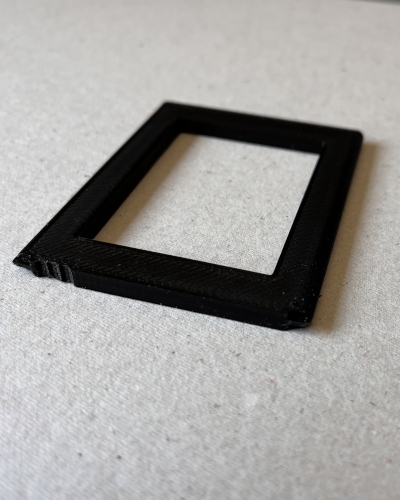
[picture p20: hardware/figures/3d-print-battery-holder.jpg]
3d printed battery holder
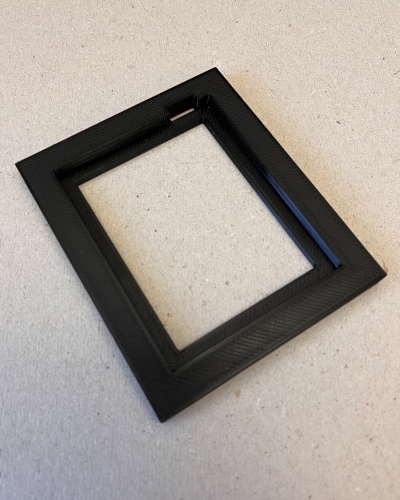
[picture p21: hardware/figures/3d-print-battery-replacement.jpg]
3d printed battery replacement
  

## Step 3: battery holder assembly (2 hours + 24 hours for epoxy to cure)

**Required tools:** Soldering station, wire cutter, wire stripper, crimping tool

**Required skills:** Working with two-part epoxy, soldering

**Required material:** Leaf battery connectors, two-part epoxy, gloves, wires

Insert the leaf battery connector component into the respective cut-out of the battery holder. Be careful when inserting it and push in the connectors with a screwdriver or similar tool. While there should be some resistance, if the component does not fit use a file or similar to remove excessive material from the 3D printed part. Once inserted, the component should look like this:

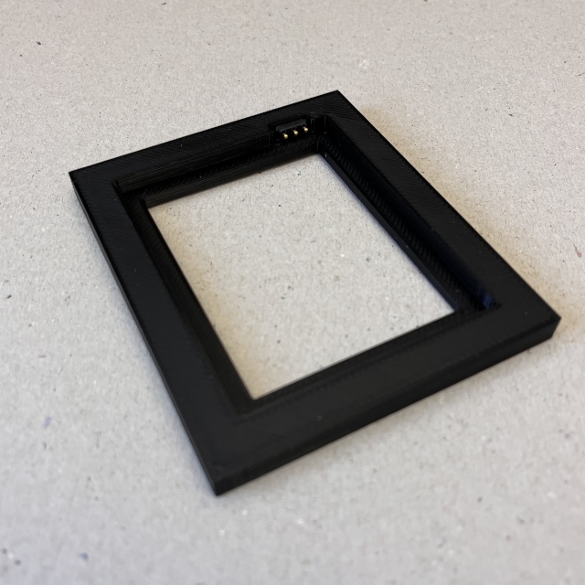
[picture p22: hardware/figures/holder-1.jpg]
Battery holder with leaf battery connector


Flip the component and solder the wires to the leaf battery connector. Make the black (ground) and yellow (data) wires about 8cm long. Make the red (positive) wire about 15cm long so that it can be later connected to the INA219 screw terminal. Use the crimp tools to add ferrules to the wires. The component should look like this:

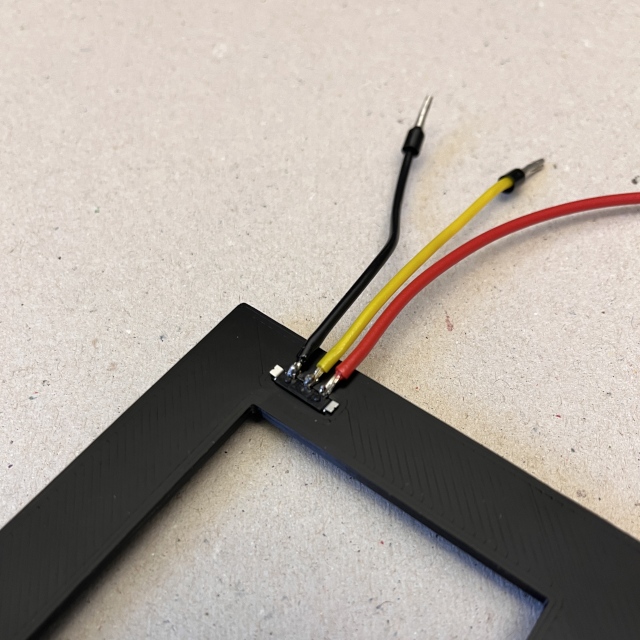
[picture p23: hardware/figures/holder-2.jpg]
Battery holder attached wires


Now, use the two-part epoxy to glue the leaf battery connector to the battery holder. Use some additional epoxy on top of the wires to give them extra support. Also glue the small "feets" to the bottom of the battery holder. The final component should look like this:

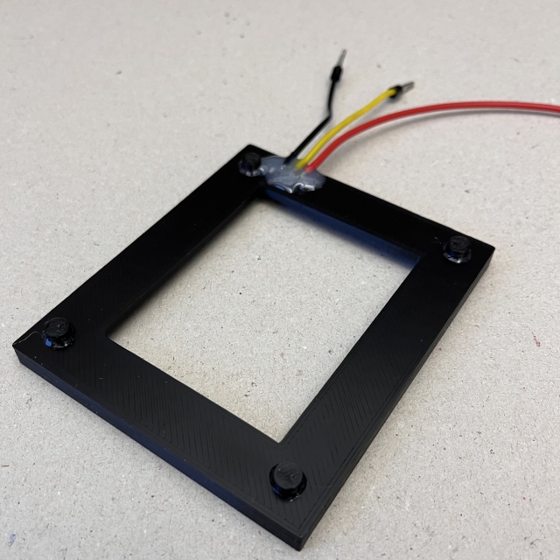
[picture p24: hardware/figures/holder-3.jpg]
Battery holder complete


Let the epoxy cure for 12 hours.

Insert a battery into the component and check that the connections align well. Use a digital multimeter to measure the voltage between the red and black wires. It should be around 3.8V. If not, check the connections and the battery. 

## Step 4: battery inlet assembly (2 hours + 24 hours for epoxy to cure)

**Required tools:** Soldering station, wire cutter, wire stripper, crimping tool, tweezers

**Required skills:** Working with two-part epoxy, soldering, working with small parts

**Required material:** SD card adapter, two-part epoxy, gloves, wires

Inspect the 3D printed battery inlet and identify the spaces for the contacts. If necessary, use a file to ensure that the corners are free of excessive material and that the surface is smooth.

Break the SD card adapter open and remove the contacts. Use the tweezers and wire cutter to remove individual contacts from it. You will need at least three. Use the 3D printed part and the tweezers to bend them so that their front is flush with the cut-outs of the 3D printed part and their end lies on the back of the component. Once all components are "harvested" and bent, apply a small amount of two-part epoxy for each contact and carefully insert them into space using a tweezer. The following pictures illustrate the process:

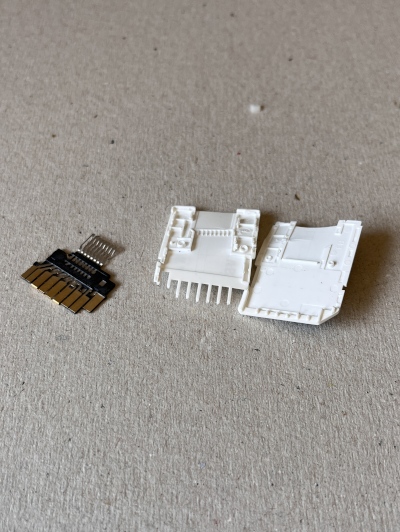
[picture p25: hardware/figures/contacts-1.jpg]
Opened SD card adapter

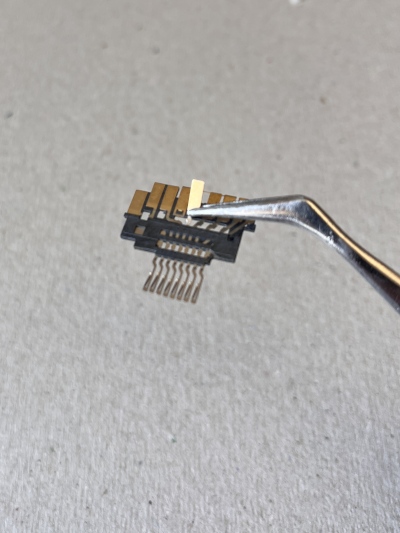
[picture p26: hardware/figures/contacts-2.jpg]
Breaking off an individual contact

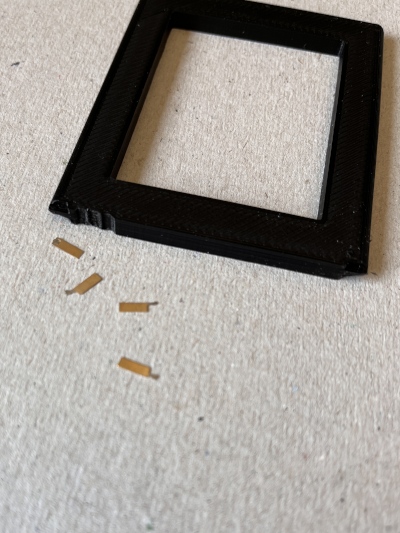
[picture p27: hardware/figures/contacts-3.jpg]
Four harvested contacts

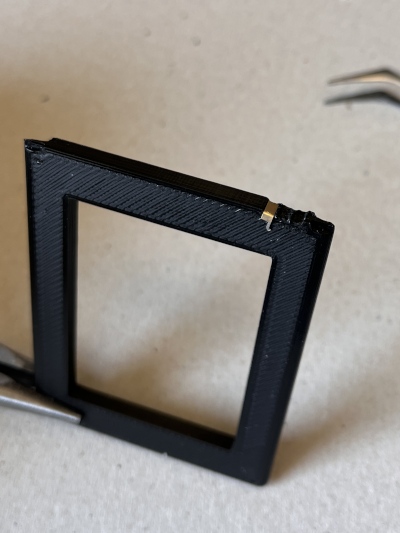
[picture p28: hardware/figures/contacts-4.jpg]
Contact bent into the right shape

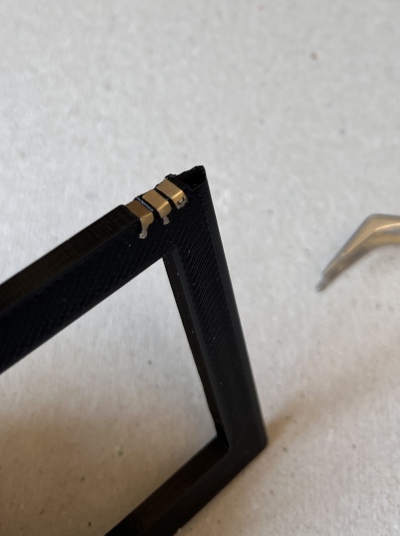
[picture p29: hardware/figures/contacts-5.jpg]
All three contacts glued into place


Be careful for the first 5 minutes while the epoxy hardens. Then wait another 12 hours for the epoxy to cure completely.

Now, solder the wires to the contacts. Make the black (ground) and yellow (data) wires about 10cm long. Make the red (positive) wire about 20cm long so that it can be later connected to the INA219 screw terminal. Use the crimp tools to add ferrules to the wires. The component should look like this:

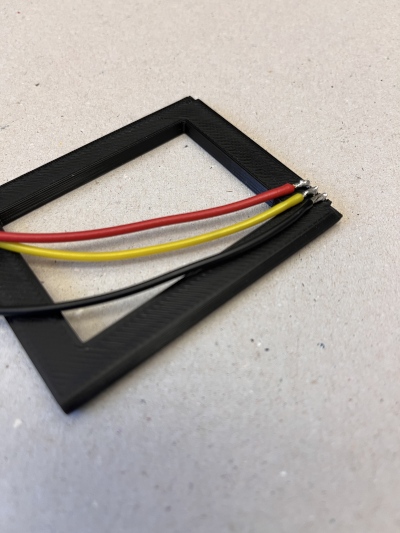
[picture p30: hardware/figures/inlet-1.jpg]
Battery inlet with wires


Then add some epoxy to the wires to give them extra support. The component should look like this:

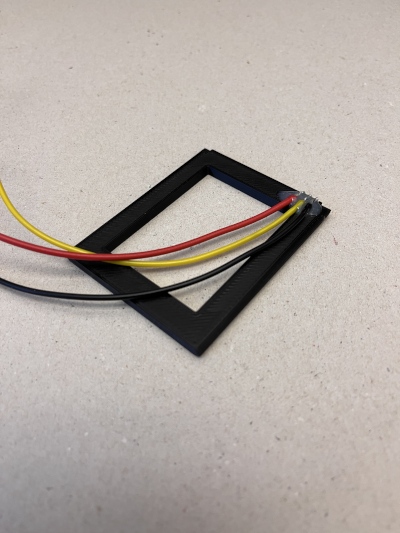
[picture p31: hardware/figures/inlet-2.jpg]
Battery inlet with wires and epoxy


Let the epoxy cure for 12 hours.

Once everything is cured, insert a battery into the component and check that the connections align well. Alternatively, you can insert it into the battery holder and check good connectivity between the wire pairs of the same color.

## Step 5: final assembly (1 hour)

**Required tools:** Screw drivers

**Required material:** Terminal connector block

Use the terminal connector block to directly connect the black (ground) and yellow (data) wires of the battery inlet and the battery holder.
Connect the red (positive) wires to the screw terminal of the INA219. The final assembly should look like this:

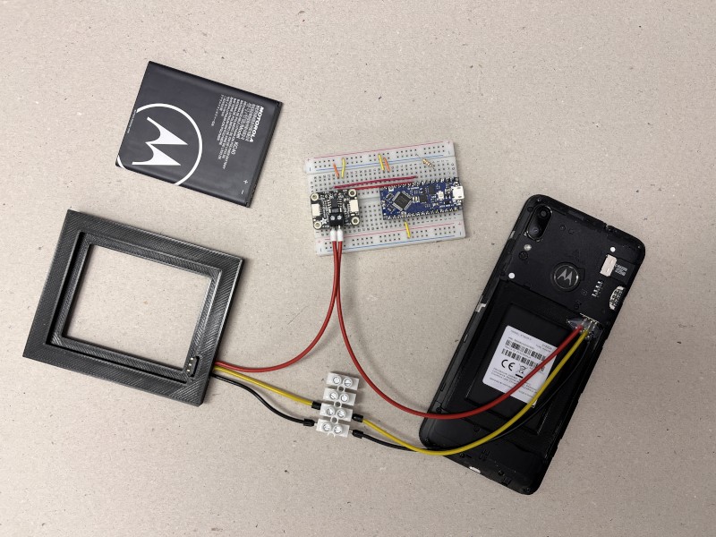
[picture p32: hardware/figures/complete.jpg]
Final assembly


> **Warning**
> The displayed image misses an important ground connection between the ground cables of the battery (black wires) and the breadboard. See [this image](figures/hw-overall.jpg) for a correct reference. Missing the ground connection will result in incorrect measurements.

Insert the battery in the battery holder and turn on the phone.

## Step 6: using the USB-to-serial adapter (1 hour)

**Required material:** USB-OTG cable, USB-to-serial adapter, male to female jumper wires

This step is only required for micro studies where we need to synchronize the clocks.

Find the jumper on the side of the USB-to-serial adapter and set it to 5V. Use the jumper wires to connect GND to ground on the Arduino board, and RTS to port A0/D14 (the one with the resistor).

With the USB-to-serial adapter, the layout should look similar to this:

overall

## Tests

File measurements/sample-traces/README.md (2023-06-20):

This directory contains sample traces for the experiments E0, E1, E2.
Use the `./decompress_sample_traces.sh` to unpack the `.tar.xz` archive into separate folders `e0`, `e1`, `e2`.
Then copy the files as you need into the `/measurements` directory.

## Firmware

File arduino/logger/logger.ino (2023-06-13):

#include <Adafruit_INA219.h>
#include <Wire.h>

Adafruit_INA219 *ina219;

#define MPS_LIMIT 2500
#define MICROS_PER_OP (1000000 / MPS_LIMIT)

#define LED_PIN 13
#define INPUT_PIN 14

unsigned long last_sent_finished;
int last_input;

// Protocol overview
// -----------------
// Data is sent in blocks of two bytes. Based on their value
// they are interpreted as follows:
//
// 0x0000..0xFFEF  the raw power measurements in low-endian uint16_t
// 0xFFF0          the input port changed to low
// 0xFFF1          the input port changed to high
// 0xFFF2..0xFFF3  [reserved]
// 0xFFFF          synchronisation before intro sequence

void setup(void) {
    // start serial
    Serial.begin(1000000);
    while (!Serial) {
        delay(1);
    }
    Serial.write("\xff\xff\xff");
    Serial.println(
        "# Compiled on '"__DATE__
        "' at '"__TIME__
        "'");

    // setup other I/O
    pinMode(LED_PIN, OUTPUT);
    pinMode(INPUT_PIN, INPUT);
    last_input = 0;

    // start I2C devices
    ina219 = new Adafruit_INA219();
    if (!ina219->begin(&Wire)) {
        Serial.println("# Failed to find INA219 chip");
        while (1) {
            delay(10);
        }
    }

    ina219->setCalibration_16V_400mA();
    // see documentation: ina219->setCalibration_CUSTOM();

    // print debug information in header lines
    debug_mps();
    Serial.print("# input pin: ");
    Serial.println(INPUT_PIN);

    // signals begin of the main protocol; no ASCII beyond this point
    Serial.println("start");

    last_sent_finished = micros();
}

void debug_mps(void) {
    unsigned long start_t = millis();
    unsigned long cnt = 0;
    while (millis() < start_t + 1000) {
        cnt++;
        ina219->getPower_raw();
    }
    Serial.print("# mps:");
    Serial.print(cnt);
    Serial.print(" (limit:");
    Serial.print(MPS_LIMIT);
    Serial.print(")");
    Serial.println();
}

void loop(void) {
    // Read pin (and report change)
    const auto curr_input = digitalRead(INPUT_PIN);
    if (curr_input != last_input) {
        digitalWrite(LED_PIN, curr_input);
        last_input = curr_input;
        Serial.write((uint8_t)(0xFF));
        if (curr_input == LOW) {
            Serial.write((uint8_t)(0xF0));
        } else if (curr_input == HIGH) {
            Serial.write((uint8_t)(0xF1));
        }
    }

    // Read power
    uint16_t power_raw = ina219->getPower_raw();
    if (power_raw >= 0xFFF0) {
        // with leading 0xFFF is special
        power_raw = 0xFFEF;
    }

    Serial.write((uint8_t)(power_raw >> 8));
    Serial.write((uint8_t)(power_raw));

    // Pause to match our target rate
    unsigned long deadline = last_sent_finished + MICROS_PER_OP;
    while (true) {
        unsigned long now = micros();
        // micros() will overflow every ~70 minutes
        if (now <= last_sent_finished) {
            last_sent_finished = micros();
            break;
        }

        // wait until deadline passed
        if (now >= deadline) {
            last_sent_finished = deadline;
            break;
        };
    }
}

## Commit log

2023-06-13 Added arduino project
2023-06-19 Added hardware documentation
    [battery.scad, battery.stl, holder.scad, holder.stl]
